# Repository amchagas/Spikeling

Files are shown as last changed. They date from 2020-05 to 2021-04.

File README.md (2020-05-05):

# Welcome to the official Spikeling GitHub

Understanding of how neurons encode and compute information is fundamental to our study of the brain, but opportunities for hands-on experience with neurophysiological techniques on live neurons are scarce in science education. Here, we present Spikeling, an open source £25 in silico implementation of a spiking neuron that mimics a wide range of neuronal behaviours for classroom education and public neuroscience outreach.

For details, please refer to
- the main manuscript on BioRxiv [here](https://www.biorxiv.org/content/early/2018/05/21/327502)
- the entry on Open Labware [here](https://open-labware.net/projects/spikeling/)

Spikeling in action

Spikeling is based on an Arduino microcontroller running the computationally efficient Izhikevich model of a spiking neuron.  The microcontroller is connected to input ports that simulate synaptic excitation or inhibition, dials controlling current injection and noise levels, a photodiode that makes Spikeling light-sensitive and an LED and speaker that allows spikes to be seen and heard. Output ports provide access to variables such as membrane potential for recording in experiments or digital signals that can be used to excite other connected Spikelings. These features allow for the intuitive exploration of the function of neurons and networks.

# Files

In this repository and the associated publication (linked above) you will find all files needed to build a Spikeling, get started with it and do some basic data analysis.

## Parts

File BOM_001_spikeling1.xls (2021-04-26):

BOM: spikeling lite
Item# | Manufacturer | Part # | Qty/PCB | Description | AI/SMD/BGA/PLCC/QFP/ OR Other Part | Designator | Top/Bottom | Comment
1
2 | Arduino | A000087 | 1 | Arduino Nano | Through-hole | MCU | TOP
3 | Samtec inc | SSA-115-S-T | 2 | Headers 15 pin 1 row | Through-hole | J8 | TOP
4 | Alps | RK09K1130AH1 | 4 | 10k/50mw/20% | Through-hole | RV1;RV2;RV3;RV4 | TOP
5 | Murata | PKMCS0909E4000-R1 | 1 | 25V 75dB | SMD | BZ1 | TOP
6 | RS pro | 546-4027 | 5 | female PCB conn | Through-hole | J1;J2;J3;J4;J5 | TOP
7 | TE connectivity | 4-1437565-1 | 1 | 12V 50ma | SMD | SW1 | TOP
8 | BroadCom | HSMF-C155 | 1 | 617nm 2V 20mA | SMD | D2 | TOP
9 | Kemet | C1206C102KDRACTU | 1 | 100V 1nf 5% | SMD | C1 | TOP
10 | Vishay | CRCW120610K0FKEA | 2 | 250V 10k 250mW 1% | SMD | R1,R4 | TOP
11 | TE connectivity | CRG1206F47R | 1 | 250V 47ohm 250mW 1% | SMD | R2 | TOP
12 | TE connectivity | CRG1206F10R | 1 | 250V 10ohm 250mW 1% | SMD | R3 | TOP
13 | Osram | BP 104 S-Z | 1 | visible spectrum photodiode | SMD | D1 | TOP
14 | Cliff | FC68148 DC10A | 1 | Barrel Jack | Through-hole | J6 | TOP
15
16
17
18
19
20
21
22
23
24
25
26
27

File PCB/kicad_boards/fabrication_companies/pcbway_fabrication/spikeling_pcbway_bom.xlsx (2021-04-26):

 |  |  | xxxx xxxx xxxxx xxPCS BOM (Sample Bill of Materials)
Item # | *Designator | *Qty | Manufacturer | *Mfg Part # | Description / Value | *Package/Footprint | Type | Your Instructions / Notes
1 | MCU | 1 | Arduino | A000087 | Arduino Nano | 2.54 through hole | Through-hole
2 | J8 | 2 | Samtec inc | SSA-115-S-T | Headers 15 pin 1 row | 2.54 through hole | Through-hole
3 | RV1;RV2;RV3;RV4 | 4 | Alps | RK09K1130AH1 | 10k/50mw/20% | Through-hole | Through-hole
4 | BZ1 | 1 | Murata | PKMCS0909E4000-R1 | 25V 75dB | SMD | SMD
5 | J1;J2;J3;J4;J5 | 5 | RS pro | 546-4027 | female PCB conn | Through-hole | Through-hole
6 | SW1 | 1 | TE connectivity | 4-1437565-1 | 12V 50ma | 6X6 mm SMD | SMD
7 | D2 | 1 | BroadCom | HSMF-C155 | 617nm 2V 20mA | 1411 smd | SMD
8 | C1 | 1 | Kemet | C1206C102KDRACTU | 100V 1nf 5% | 1206 | SMD
9 | R1,R4 | 2 | Vishay | CRCW120610K0FKEA | 250V 10k 250mW 1% | 1206 | SMD
10 | R2 | 1 | TE connectivity | CRG1206F47R | 250V 47ohm 250mW 1% | 1206 | SMD
11 | R3 | 1 | TE connectivity | CRG1206F10R | 250V 10ohm 250mW 1% | 1206 | SMD
12 | D1 | 1 | Osram | BP 104 S-Z | visible spectrum photodiode | DIL SMT | SMD
13 | J6 | 1 | Cliff | FC68148 DC10A | Barrel Jack | Through-hole | Through-hole
Need a quick and accurante quote? Need an efficient production? Please read SMT Ordering Necessary Files & Info in 1 minute. Thank you very much! (https://www.pcbway.com/smt_ordering_guide.html)
Click for Instructions on How to Create a BOM (https://www.pcbway.com/blog/PCB_Assembly/How_to_Build_a_BOM__Bill_Of_Materials_.html)

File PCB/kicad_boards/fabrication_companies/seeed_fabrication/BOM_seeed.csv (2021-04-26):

Designator | Manufacturer Part Number or Seeed SKU | Qty | Link
J7 | 102010268 | 1 | https://www.seeedstudio.com/Seeeduino-Nano-p-4111.html
J7,J8 | SSA-115-S-T | 2 | https://www.digikey.co.uk/products/en?keywords=SSA-115-S-T
RV1;RV2;RV3;RV4 | RK09K1130AH1 | 4 | https://uk.farnell.com/alps/rk09k1130ah1/pot-rotary-10k-17mm-20/dp/1191725?CMP=GRHB-OCTOPART
BZ1 | PKMCS0909E4000-R1 | 1 | https://www.digikey.co.uk/product-detail/en/murata-electronics/PKMCS0909E4000-R1/490-9647-1-ND/4878401
J1;J2;J3;J4;J5 | 546-4027 | 5 | https://uk.rs-online.com/web/p/coaxial-connectors/5464027/?sra=pstk
SW1 | 4-1437565-1 | 1 | https://www.digikey.co.uk/product-detail/en/FSM4JSMA/450-1129-ND/525821?WT.z_cid=ref_octopart_dkc_buynow&curr=gbp&site=us
D2 | HSMF-C155 | 1 | https://www.digikey.co.uk/product-detail/en/HSMF-C155/516-1456-1-ND/637780?WT.z_cid=ref_octopart_dkc_buynow&curr=gbp&site=us
C1 | C1206C102KDRACTU | 1 | https://www.digikey.co.uk/product-detail/en/C1206C102KDRACTU/399-3437-1-ND/721308?WT.z_cid=ref_octopart_dkc_buynow&curr=gbp&site=us
R1,R4 | CRCW120610K0FKEA | 2 | https://www.digikey.co.uk/product-detail/en/CRCW120610K0FKEA/541-10.0KFCT-ND/1181874?WT.z_cid=ref_octopart_dkc_buynow&curr=gbp&site=us
R2 | CRG1206F47R | 1 | https://www.digikey.co.uk/products/en?keywords=CRG1206F47R
R3 | CRG1206F10R | 1 | https://www.digikey.co.uk/products/en?keywords=CRG1206F10R
D1 | BP 104 S-Z | 1 | https://www.digikey.co.uk/product-detail/en/Q65110A2626/475-1345-1-ND/1227851?WT.z_cid=ref_octopart_dkc_buynow&curr=gbp&site=us
J6 | FC68148 DC10A | 1 | https://uk.farnell.com/cliff-electronic-components/fc68148/socket-pcb-dc-power-2-1mm-pk10/dp/224959?CMP=GRHB-OCTOPART

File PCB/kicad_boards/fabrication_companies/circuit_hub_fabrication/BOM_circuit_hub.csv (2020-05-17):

References | Qty | Description | Manufacturer | MPN | Manufacturer_1 | MPN_2 | Digikey | Mouser | RS | Newark | Farnell
J7;J8 | 2 | Headers 15 pin 1 row | Samtec inc | SSA-115-S-T | Samtec Inc | SSW-115-01-T-S | SAM1122-15-ND |  | 180-4101 |  | 2779587
RV1;RV2;RV3;RV4 | 4 | 10k/50mw/20% | Alps | RK09K1130AH1 |  |  |  |  | 729-3587 |  | 1191725
BZ1 | 1 | 25V 75dB | Murata | PKM22EPPH4001-B0 |  |  |  |  | 516-8252 |  | 1192512
J1;J2;J3;J4;J5 | 5 | female PCB conn | Radiall | R141426161 |  |  | A101972-ND | 501-R141426161 | 721-0291 |  | 4195115
SW1 | 1 | 35V 10mA | E-switch | KS-01Q-01 | C&K | D6C90 F1 LFS |  |  | 102-327 |  | 2522279
D2 | 2 | 617nm 2V 20mA | Knightbright | L-793ID |  |  |  |  | 247-1791 |  | 1142588
C1 | 1 | 100V 1nf 5% | Multicomp | MCRR50102COGJ0100 | Murata | RDE5C1H102J0M1H03A | 490-8962-1-ND | 81-RDE5C1H102J0M1H3A | 1335665P |  | 1216422
R1,R4 | 2 | 250V 10k 250mW 1% | Multicomp | MF25 10K | TE connectivity | CFR16J10K | A104668CT-ND |  | 125-1153 |  | 9341110
R2 | 1 | 250V 47ohm 250mW 1% | Multicomp | MF25 47R | Ohmite | OD470JE | OD470JE-ND | 588-OD470JE | 707-7568 |  | 9341986
R3 | 1 | 250V 10ohm 250mW 1% | Multicomp | MF25 10R | TE connectivity | YR1B10RCC | A105944CT-ND | 279-YR1B10RCC | 1372768 |  | 9341145
D1 | 1 | IR 20° | Osram | SFH203 | Osram | SFH203-FA | 475-1075-ND | 720-SFH203FA | 654-8154 | 94AC4969 | 1212743

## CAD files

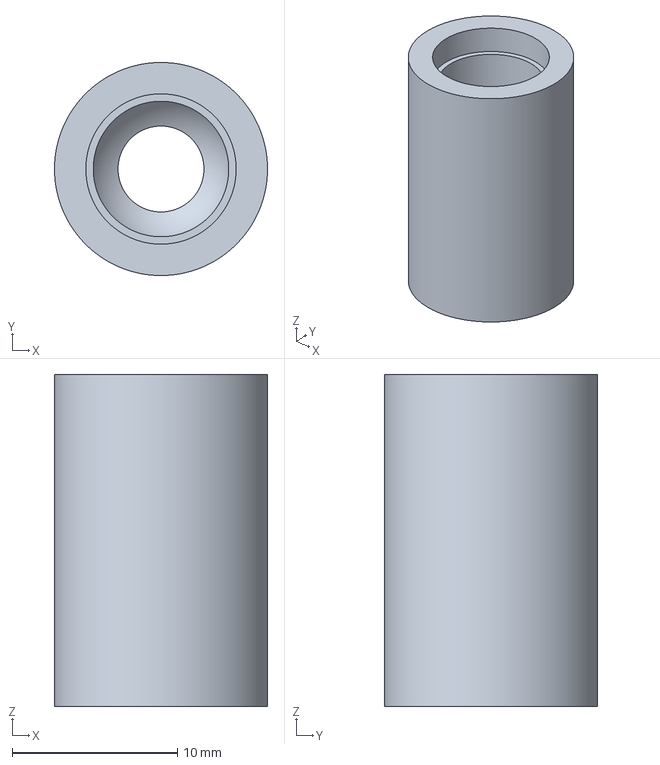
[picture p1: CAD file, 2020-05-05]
3D print/Spikeling LED holder.3mf
12.9 x 12.9 x 20.1 mm

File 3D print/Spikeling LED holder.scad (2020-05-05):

tol = 0.1;
Smoothness = 200;
Wall = 2;

r_LED = 8.9/2;
r_led = 8.0/2;
h_LED = 11.2;
h_LED_base = 2.1;
h_LED_top = 3;

r_photo_base = 6/2;
r_photo = 5/2;
h_photo = 8.9;
h_photo_base = 1;



difference(){
    cylinder (r=r_LED+Wall, h=h_photo, $fn=Smoothness);
    
    #cylinder (r=r_photo_base+tol, h=h_photo_base+tol, $fn=Smoothness);
    translate([0,0,h_photo_base+tol])cylinder(r=r_photo+tol, h=h_photo-h_photo_base+tol, $fn=Smoothness);
}
difference(){
    translate([0,0,h_photo])cylinder(r=r_LED+Wall, h=h_LED, $fn=Smoothness);
    
    translate([0,0,h_photo+h_LED_top])cylinder(r=r_led+tol, h=h_LED-h_LED_top
    , $fn=Smoothness);
    translate([0,0,h_photo+h_LED-h_LED_base])cylinder(r=r_LED+tol, h=h_LED_base, $fn=Smoothness);
    translate([0,0,h_photo+r_led])sphere(r=r_LED+tol, $fn=Smoothness);
    translate([0,0,h_photo])cylinder (r=r_photo+tol, h=h_LED, $fn=Smoothness);
}

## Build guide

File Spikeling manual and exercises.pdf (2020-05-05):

# Spikeling User Manual

## Content

Version 1. 6

th Sept 2018.

## Assembly From Parts

If desired, all parts can be conveniently sourced through Kitspace: https://kitspace.org/boards/github.com/badenlab/spikeling/

When using this option, please be aware:

1) Kitspace will almost certainly not find the cheapest Arduino Nano (clone). You should be able to get one for less than £3. Similarly, PCB manufacturing options suggested may also not be the cheapest. Google is your friend here!
2) Kitspace will likely find some options where “packs” of components are listed (e.g. instead of the 2 optional screws to hold the optional battery pack in place, it may find a box of 100). So, when using the option, do carefully go through the suggested purchase list and edit as appropriate.
3) Obviously, when buying in bulk, things can get a lot cheaper (potentially several-fold savings per unit).

Solder all parts in place as per the below. An introduction to soldering is here: https://www.howtogeek.com/63630/how-to-use-a-soldering-iron-a-beginners-guide//.

For details on parts, see Bill of materials (BOM).

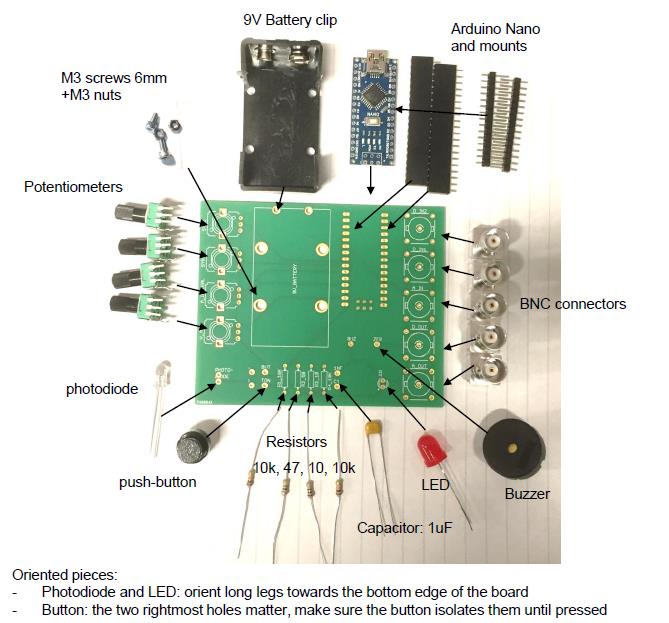
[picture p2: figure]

When complete, it should hopefully look like this:

Note: If it doesn’t seem to work, 9 out of 10 times it’s because 1 of the following:

1) Did you upload the Arduino script? If not sure how to do that, see below under getting started.
2) Somewhere, 2 or more contacts that shouldn’t touch, so in fact touch and thus short-circuit something. Carefully check the board (both sides, solder can leak through the holes and make unwanted contacts on the other side). To check, it can be instructive to “beep” the circuit with a multimeter (google that if unsure). If you have a short circuit, remove it. Usually, simply reheating the pad may do the trick, but if not, used a solder sucker.
3) “Cold contacts”, i.e. an intended contact that are not actually connected. This can easily happen e.g. if the parts are slightly moved during soldering, such that in the last second, as the solder hardens, the pieces come apart. They may then “look” like they are fine, but don’t conduct. Check with multimeter, or simply re-heat all the dodgy looking contacts.
4) Did you solder the oriented pieces the right way round? (see previous page)

You will know if it works if you power it (Battery or USB cable), with all dials turned to midpoint, if you then crank up dial 4 or hold it into the light, it should start to spike (audible clicks coupled to flashes from the LED). Congratulations, you have successfully built a Spikeling!

## Getting Started

Turn all dials to midpoint (you should feel a gentle “click”) and power the board (via USB, or via 9V Battery). The Arduino LEDs should come on. If the board is already on, press the small white reset button on the Arduino itself (not the big black button on the board). This will take a few seconds and puts Spikeling in “reset state” (i.e. mode 1, with all dials to midpoint). All instructions below assume you start from here.

The reset state mimics the “average textbook neuron” - a vertebrate spiking neuron with a resting membrane potential around -70 mV and a spike threshold around -55 mV.

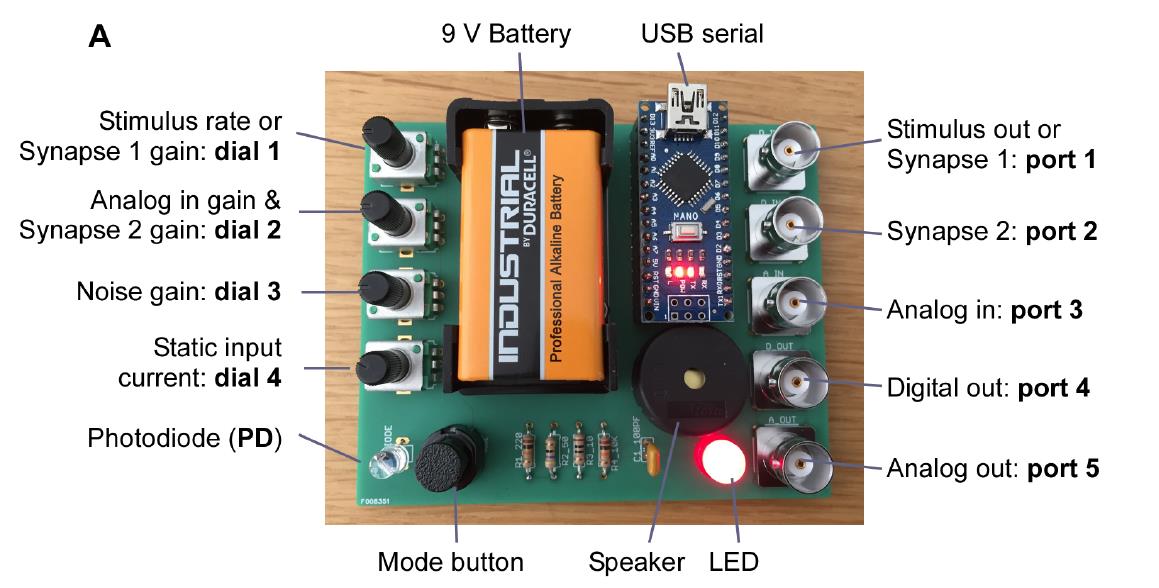
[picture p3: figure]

To visualise and record the activity of Spikeling, there are several options but the best is via a serial connection to a PC through the USB connection on the Arduino. Here we describe how to use the Serial-Oscilloscope software package provided (under creative commons from http://x-io.co.uk/serial-oscilloscope/). This lets you read all output parameters directly from the Spikeling board for display on the screen or for logging. There is also a YouTube video (https://www.youtube.com/watch?v=jgMG0UQ2_pc) demonstrating how to set up the oscilloscope.

1) Make sure the Arduino IDE is installed as you need the driver (www.Arduino.cc). Note that if you are using an Arduino-clone, the standard drivers may not work. In this case, google for the correct ones and install those instead.
2) Declare the serial port. When you plug the USB cable into the PC you may see a message telling you which “COM-port” is being used. This is the “serial port” which you need to set in the menu of the serial oscilloscope. It may just give one option which is then probably the correct one. The COM port is also found under the Device manager.
3) Set the Baud Rate to 230400.
4) The window should now produce a continuous stream of numbers. These are the output values from Spikeling. To plot them, open the oscilloscope(s) under the menu. Spikeling outputs 9 parameters in parallel, but each oscilloscope window can only display 3. If you need parameters further down the list, simply open a second oscilloscope. You can separately adjust the scale of each trace on the oscilloscope by first selecting it (click the “Beam” button) and then scaling it (left-most thin arrows) and off-setting it (big red arrows). You can also trigger the oscilloscope using the menu on the bottom right.
5) To record data, click “log to file”. This will write a text file (comma and tab separated ASCII) with all numbers output from Spikeling. You can look at this output using any common data-analysis software (for example GNU-R, which is free, or Igor Pro or MATLAB, which are licensed).

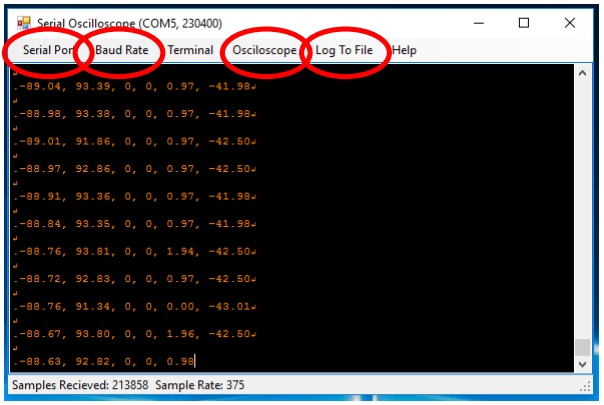
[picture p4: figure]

The output parameters of Spikeling are as follows:

1) Membrane voltage Vm (in “mV“)
2) Total input current Itotal (in arbitrary units). Itotal = IVm + IPD + ISyn1 + ISyn2+ IanalogIn
3) Stimulus state of Synapse 1 port (see below, range 0-1)
4) Synapse 1 state (see below, boolean 0-1 for nospike / spike in the input)
5) Synapse 2 state (see below, boolean 0-1 for nospike / spike in the input)
6) Total photodiode current IPD (in arbitrary units)
7) Total Analog In current IanalogIn (in arbitrary units)
8) Total Synaptic current ISyn (in arbitrary units) ISyn = ISyn1 + ISyn2
9) System time since last reset (in microseconds)

You can also read Spikeling’s Vm output via the BNC ports using a regular oscilloscope. Digital Out only carries the spikes (TTL 5V) while Analog Out on port 5 carries a version of the analog membrane voltage (in arbitrary units). (Note that this output is a pulse-width modulated (PWM) digital signal that is RC-filtered to produce and analog out: it will therefore display filtering artefacts).

Note: If Spikeling is doing “weird things” that clearly does not align with this manual, chances are there is a bad solder contact somewhere – either connecting two pins that should not be connected, or not connecting pins that should be connected (e.g. due to cold solder contacts). Check all contacts carefully and redo them if necessary (i.e. heat them up briefly so they can resettle). It can be worthwhile checking connections with a Multimeter, if available.

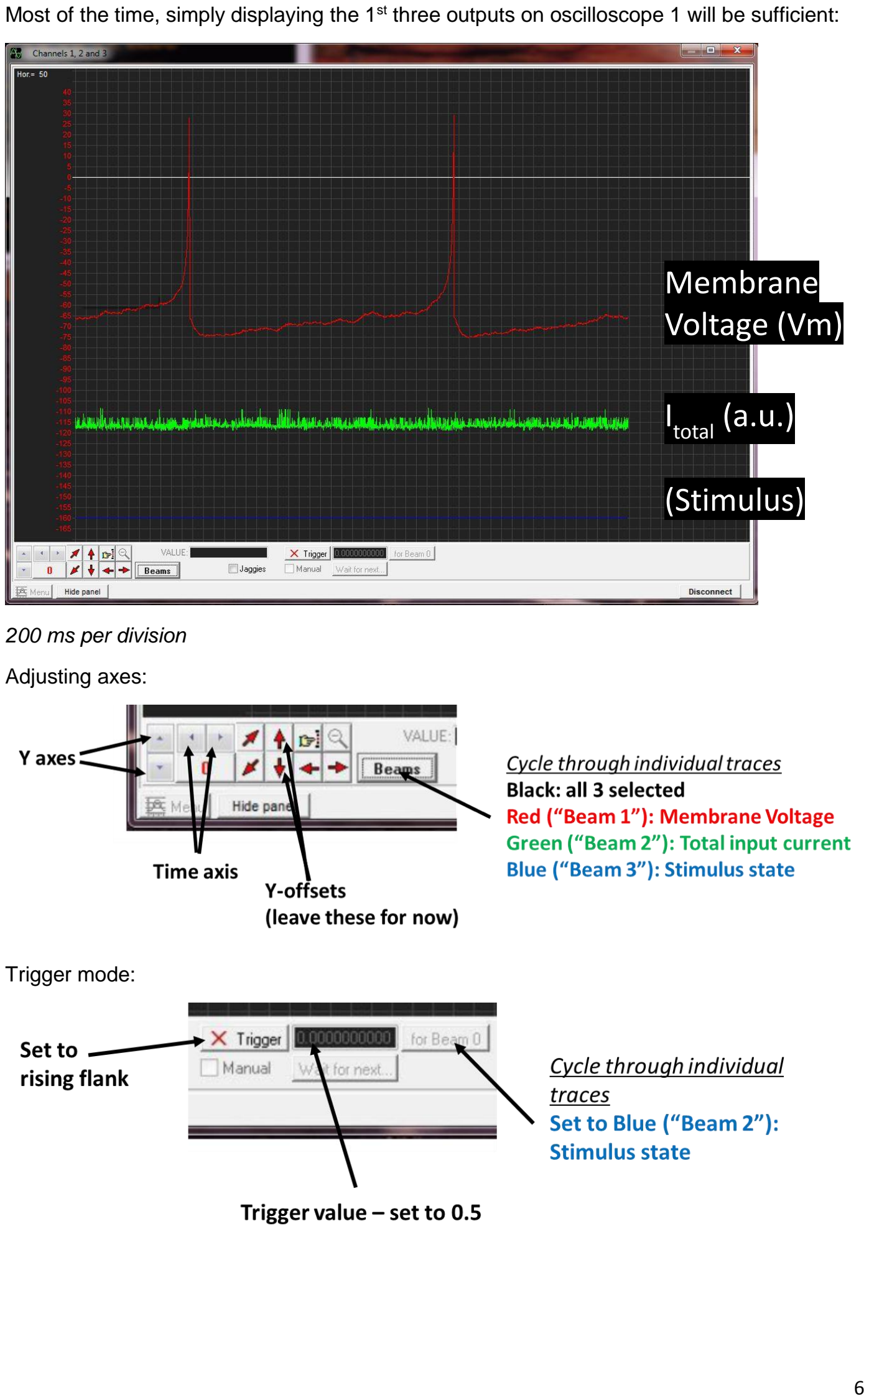
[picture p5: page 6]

Most of the time, simply displaying the 1st three outputs on oscilloscope 1 will be sufficient:

200 ms per division

Adjusting axes:

Trigger mode:

# Membrane Voltage (Vm)

I

# total (a.u.)

# (Stimulus)

## Visualising Spikeling Output with MATLAB

The Serial Oscilloscope plotter saves recordings in comma-separated CSV files. These can be read by a wide range of software: open source possibilities include GNU-R (https://www.r-
project.org), | Python | (https://www.python.org) | or | Octave
(https://www.gnu.org/software/octave/). To comply with software preinstalled on the teaching PCs available at the University of Sussex, we chose to use MATLAB (Mathworks). MATLAB licenses are, however, costly and below we also provide instructions on the use of Python (free!) for visualising Spikeling output.

After opening MATLAB, make sure you have the recorded data and the MATLAB scripts in the same folder. Navigate to that folder (alternatively, the scripts/data may be added to the path.)

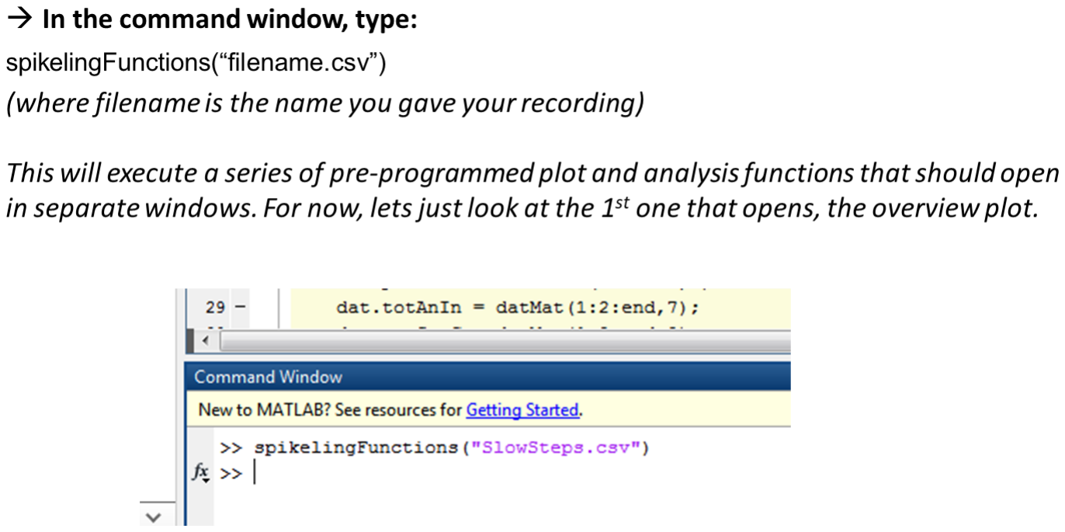
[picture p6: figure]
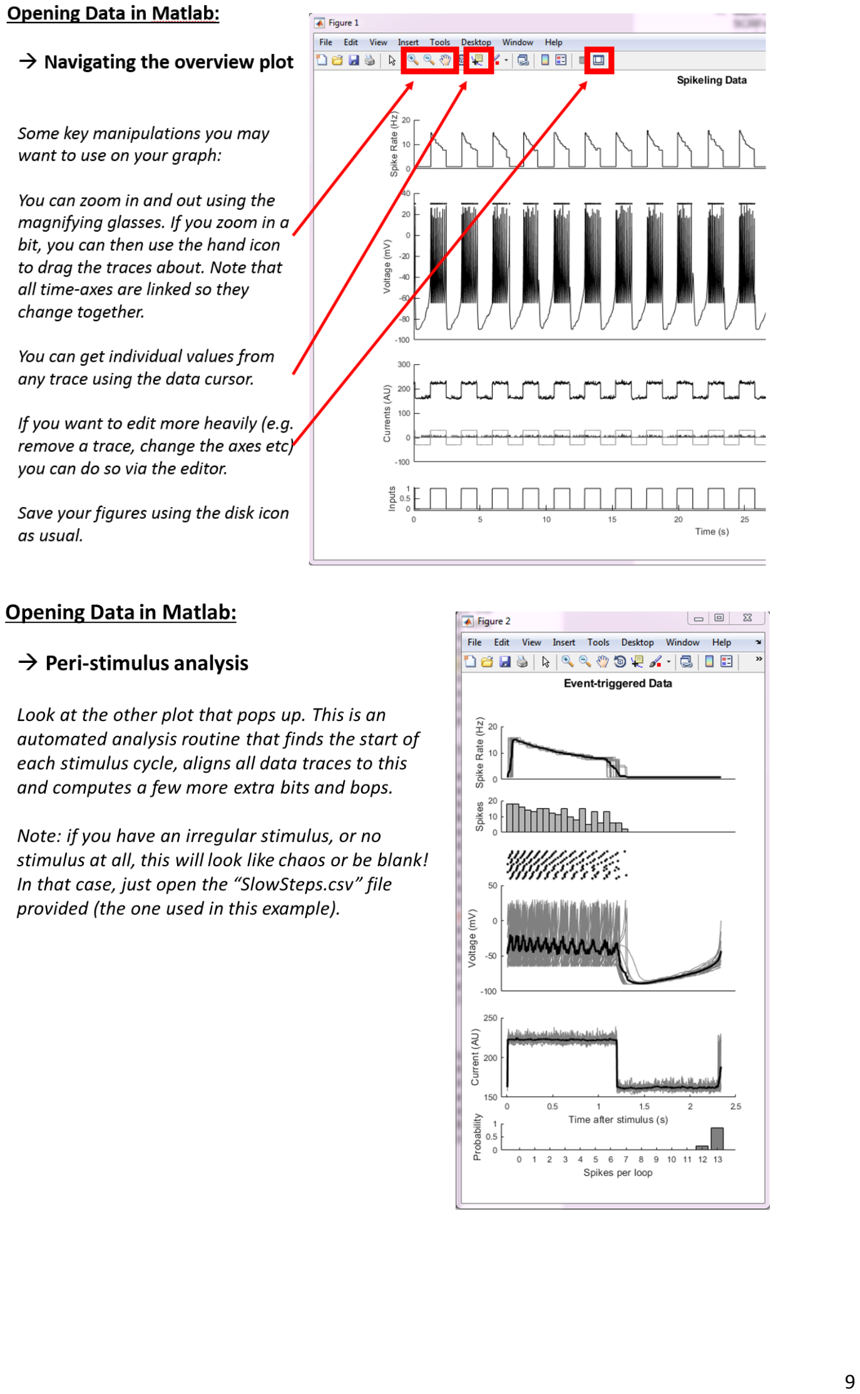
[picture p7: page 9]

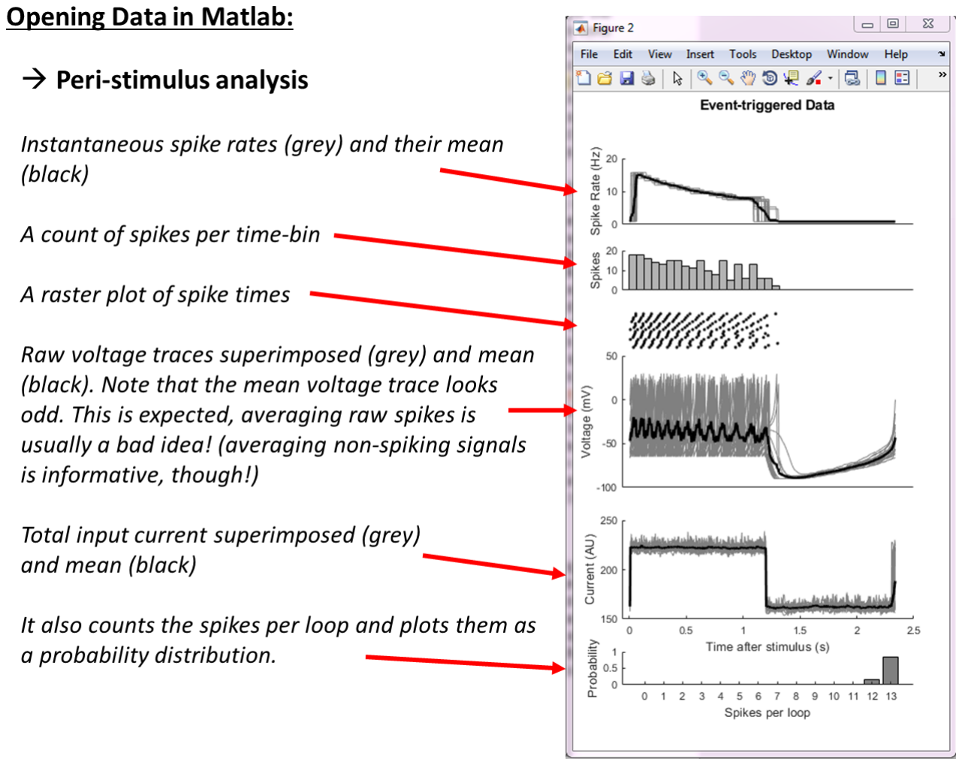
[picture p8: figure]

## Visualising Spikeling Output with Python

We also provide similar scripts in Python (which is free) in the form of a Jupyter Notebook (http://jupyter.org) that reads the serial plotter’s logged csv file, detects spikes, aligns the data in different ways and plots the results in simple graphs. Here we provide a brief explanation of how to run the Python code, rather than a repeat of the detailed explanation of the plot functions.

### Getting started with Python

While the Jupyter Notebook could principally also be executed directly from GitHub without installing Python, this would quickly generate issues with the way that the script provided loads the csv data. For simplicity and convenience, we therefore here give a brief account of how to execute and modify the script in Anaconda.

1) Download Anaconda (it’s free). Navigate to https://conda.io/docs/user-guide/install/, pick the right version for your operating system and follow the install instructions given
2) Once installed, launch a Jupyter Notebook, for example by executing the Anaconda Navigator and clicking “launch” under the corresponding tab. This will open a window in your web browser showing some folders on your home hard drive. Here, navigate to the folder containing the Jupyter script provided (Spikeling Analysis.ipynb) and open that script.

3) Also copy whatever csv file recorded with Spikeling you want to analyse. In the example given below, this will be the file SlowSteps1.csv in the zipped Example Data provided.
4) Your screen should now hopefully look something like this:

### Using the Juypter Notebook

Jupyter notebooks are organised into “cells” (each grey area) which can be called individually. Alternatively, all cells can be called at once (in sequence) to execute the whole thing.

Before doing so, make sure that the file name to be analysed is entered where it says:

data = np.loadtxt(‘SlowSteps1.csv’, delimiter = ‘,’)

i.e. if you wanted to read a file name “SomeNewData27.csv” that line should read:

data = np.loadtxt(‘SomeNewData27.csv’, delimiter = ‘,’)

Now, click on the topmost cell (i.e. where it reads “Load raw data”) and then click “run”. This will execute that one cell and jump to the next (which in this case it doesn’t do anything interesting). If you now keep clicking “run”, it will execute each cell of the script in sequence.

To run the whole thing in sequence (not ideal as the bottom of the script has some optional bits) you can also press the >> button 3 steps to the right of “Run”

Once you reach the first plot, it should open up a new tab that simply plots the raw data (and detected spike times). It should hopefully look something like this:

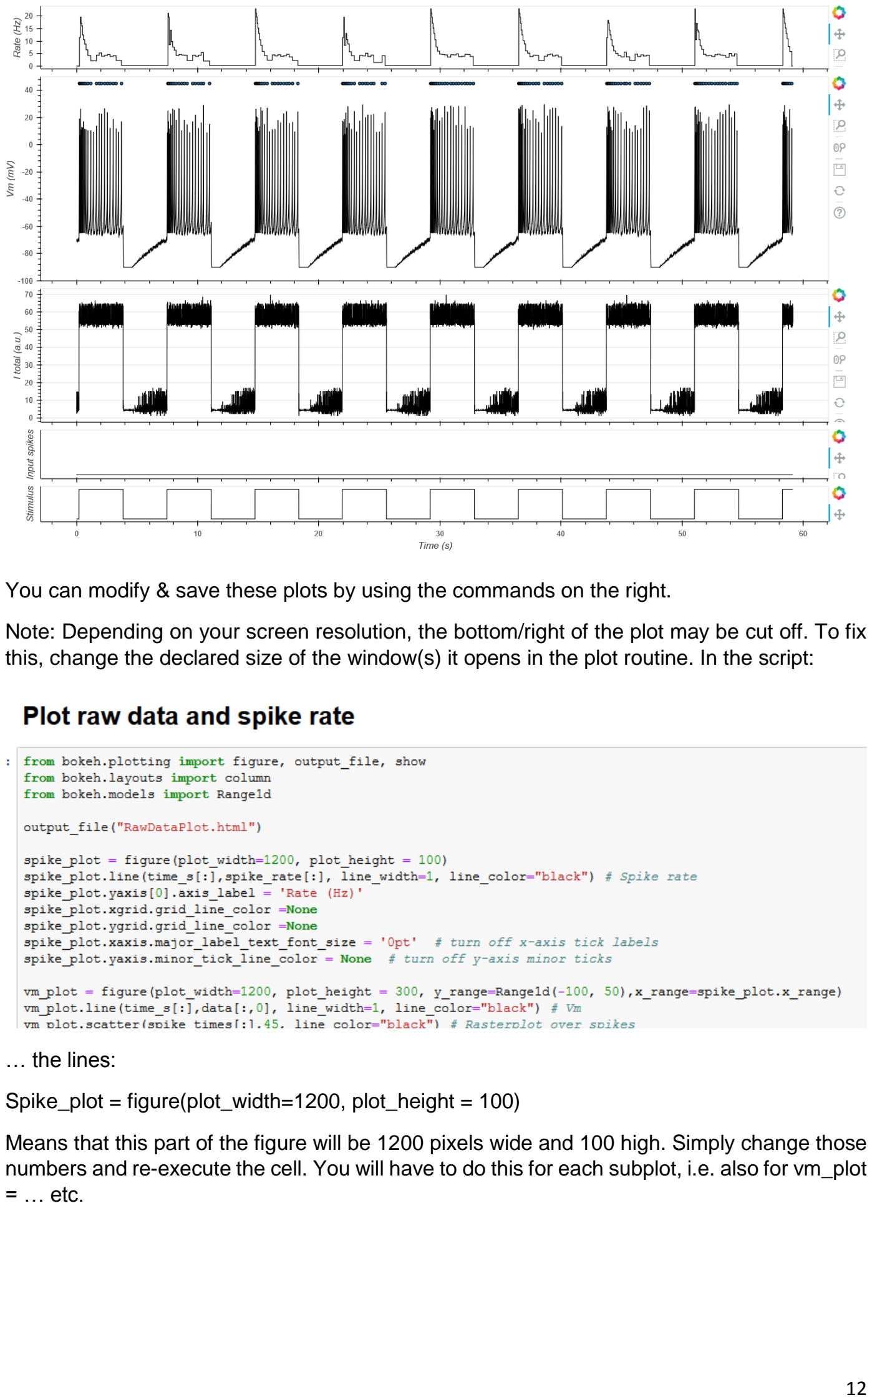
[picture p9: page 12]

You can modify & save these plots by using the commands on the right.

Note: Depending on your screen resolution, the bottom/right of the plot may be cut off. To fix this, change the declared size of the window(s) it opens in the plot routine. In the script:

… the lines:

Spike_plot = figure(plot_width=1200, plot_height = 100)

Means that this part of the figure will be 1200 pixels wide and 100 high. Simply change those numbers and re-execute the cell. You will have to do this for each subplot, i.e. also for vm_plot = … etc.

### Plotting Stimulus aligned data

Following execution of the subsequent the “Analysis Open 1…” cells, a few cells further down, under heading “plot stimulus aligned data” it will generate the stimulus aligned plot. The dimensions of this can be altered in the same way as described above, if required.

### Plotting STAs

Alternatively, if the data is a “noise sequence” generated to recover linear filters (spike triggered averages, STA), skip the whole part that says “Analysis Option 1…” and go straight to “Analysis Option 2: Spike triggered average (STA)”.. Executing this cell will give the STA:

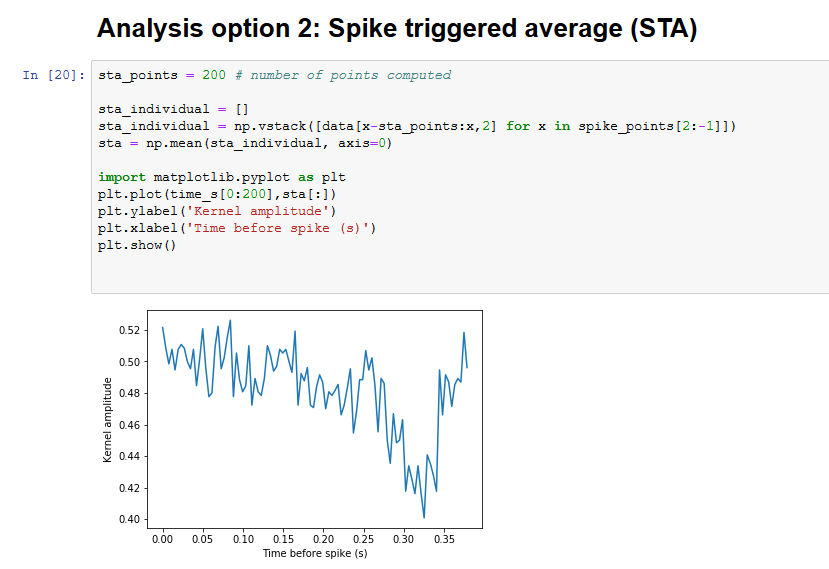
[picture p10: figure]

(here shows the result for the STA of the example data “Noise_Mode3.csv”)

## Reprogramming Spikeling (Arduino)

The “brain” of Spikeling is the Arduino-Nano microcontroller (the blue thing). By tweaking the code that is uploaded here (via the USB cable from the Arduino IDE) it is fairly straightforward to modify Spikeling behaviours, for example by modifying some of the “mode settings”. When opening the Arduino code, in the top there is a list of variables and arrays with some annotations. These should be the 1st point of contact when modifying the code. After each modification, the code needs to be saved and uploaded to the Arduino for the change to take effect.

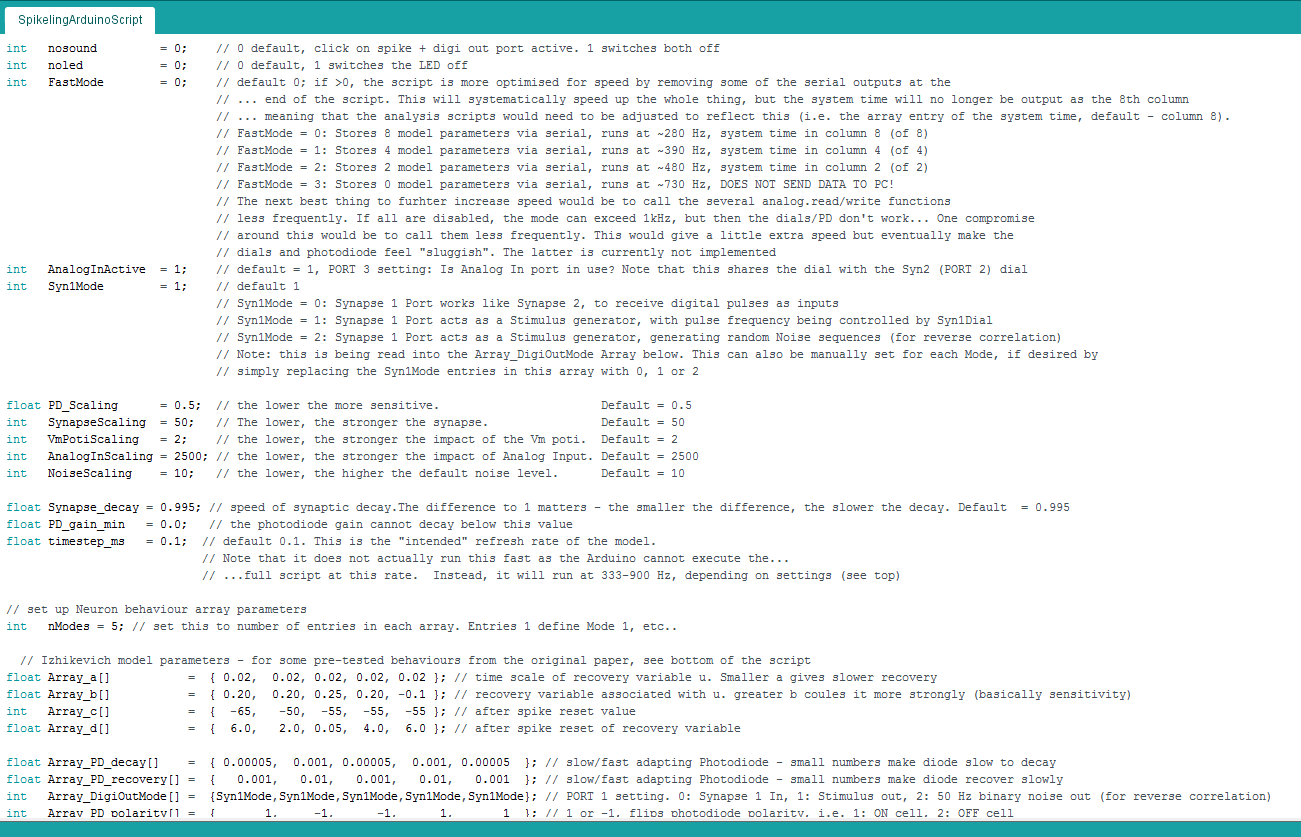
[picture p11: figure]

The screenshot above shows the main variables to tune if desired. For example, replacing the nosound variable currently set to “0” with a “1” will stop the clicking whenever it spikes (note it will also disable the Digi out port as these are on the same connector!).

To modify an existing “mode”, you need to edit the corresponding entries in the 8 arrays listed below “Izhikevich model parameters”. For example, switching the first entry in Array_PD_polarity from currently “1” to “-1” will invert mode 1’s photo-response to make it an “Off-cell”. In the same way, changing the “1” to a “2” will double the gain of the photo-response, etc.

To add new modes, or delete existing ones, simply set the nModes parameter to the new number of entries in each array (must be the same!) and modify the arrays accordingly. For a handy lookup of useful Izhikevich model parameters, scroll to the bottom of the code.

Note: Due to space constraints on the PCB, two Spikeling ports/dials are double booked by two functions. These are:

i) Synapse 1 & Stimulus out use the same port (1), and cannot operate at the same time. This is defined in the Array_DigiOutMode array. “0” enables Synapse 1, “1” enables the 50% duty cycle pulses digi out (default) and “2” enables the 50 Hz noise stimulus used for estimating linear filters (cf. Fig. 6).

ii) Analog In and Synapse 2 gain use the same dial (2). Usually this does not create a conflict as in most cases either Analog In and synapse 2 are not used at the same time. If a conflict arises, it is possible to switch off the Analog In gain using the AnalogInActive variable (set to 0). Advanced users may also choose to re-port these functions in the core code – this would involve resetting the port variables in “void setup” and checking that any use of these ports in the remainder of the code aligns with that change.

### Arduino Implementation of Izhikevich Model

The Izhikevich model is implemented by iteratively computing voltage (v) based on two equations:

(1) v = v + timestep_ms * (0.04 * v * v + 5*v + 140 – u + I_total);
(2) u = u + timestep_ms * (Array_a[NeuronBehaviour] * (Array_b[NeuronBehaviour]*5 – u));

and two conditionals:

(3) if (v>=30.0) {v=Array_c[NeuronBehaviour]; u+=Array_d[NeuronBehaviour];}
(4) if (v>=-90) {v=-90.0);}

In detail:

Lines (1) and (2) are the main model implementations, where…

…we first compute the new value for voltage (v) by adding a quadratic formula of v with recovery variable (u) subtracted, followed by the addition of a single number I_total that reflects the summed input currents (from static input current, photodiode, analog in, synaptic currents etc.)

… and then we re-compute a new value of the recovery variable (u) based on Array entries Array_a and Array_b at position NeuronBehaviour (=the mode, switchable by the onboard button). At default, NeuronBehaviour == 0, so the 1st entries in Array_a and Array_b are used, and when pressing the button NeuronBehaviour is incremented by +1 each time until it resets if it exceeds nModes (further up in the script). The Arrays are found near the top of the script, and reflect the original parameters a, b (& c, d, see below) from the model. Generally, a larger value of u hyperpolarises the model in the next computation of u, as it directly opposes I_total.

In both lines (1) and (2), the increment to v and u is scaled by global variable timestep_ms (default = 0.1). This reflects the “intended” model refresh rate. So, if that set of equations were called 10 times per millisecond (i.e. at 10 kHz) the model would run at “real-time”. However, the actual call-rate is much lower, as the Arduino cannot execute the full script at 10 kHz. In standard configuration, it actually runs at only ~420 Hz. Ways to increase speed are discussed below (“Spikeling Refresh Rate”).

Next, lines (3) and (4) are two conditionals that are triggered as a spike occurs (3) or if membrane voltage drops too low (4).

Line (3) is a carbon copy version of the original Izhikevich model, where upon execution of a spike (v exceeding 30 mV) the model resets the new value of v to be equal to Array_c[NeuronBehaviour] and resets the value of u according to Array_d[NeuronBehaviour].

Line (4) is a custom addition to the model that stops it from hyperpolarising below -90 mV. This is non-essential, but stops the model from crashing if, for instance,I_total becomes too negative to drive unrealistically low membrane voltages.

The functions of Array entries a, b, c and d are explained in detail in the original paper (Izhikevich 2003). The paper and later online additions also give a list of possible “useful combinations” of a, b, c and d that together give the model different “realistic” behaviours. For convenience they are also pasted into the bottom of the Arduino script. To implement them, simply take a specific behaviour’s 1st 4 numbers and add them to the four arrays in the top of the script:

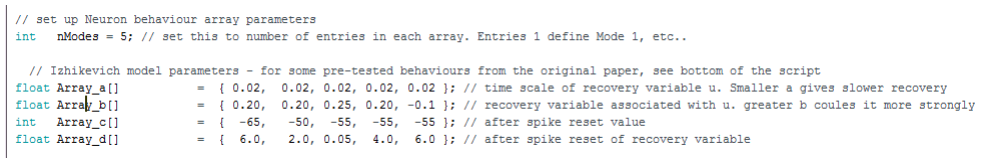
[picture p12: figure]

### Photodiode Adaptation Speed

The photodiode is inherently noisy, so here we use a “buffered time-averaging” of its signal to ameliorate some of the noise. Instead of just reading it’s state on the corresponding AnalogIn Pin (1st line, PDVal) and sending that drive directly into the model as I_PD, we instead send each instance of PDVal into a buffer array PDVal_Array of size 10. Each time the buffer is full (after 10 instances of PDVal being stored in the buffer), we take its mean (PDVal_smoothed) and use that number to inform I_PD.

Next, the Photodiode also has two gain factors (global scaling, and local gain) and two decay constants (time dependent) associated, which allows to have the PD current adapt over time, as it would in most sensory neurons.

- PD_Scaling is global and set at the beginning of the script. This is a single number that scales the amplitude of all PD_related amplitude processes
- PD_gain is the current gain of the PD system. At default, this is 1, but it falls below 1 if the PD in continuously driven, and recovers thereafter as a function of the time-dependent variables, both of which are stored in Arrays at the top of the script and depend on the Mode variable NeuronBehaviour:
- Array_PD_decay[NeuronBehaviour]
- Array_PD_recovery[NeuronBehaviour]
- PD_gain is limited at the top at 1 (full gain), and and the bottom at PD_min (default = 0, which will also have I_PD at 0).
- Finally, as I_PD is being used in the Izhikevich model (see previous section) it is multiplied by either 1 (no change) or -1 (invert), to allow flipping its polarity as a whole thus mimicking “On” and “Off” type behaviour, respectively. This flip is controlled by a third array: Array_PD_Polarity[NeuronBehaviour]

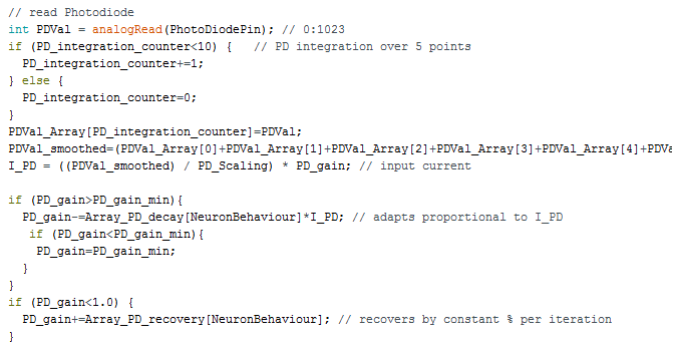
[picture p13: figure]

Photodiode-related arrays at the top of the script:

### Model Noise

Spikeling allows adding synthetic noise to the model, to mimic noisiness in neurons. The noise is added to the I_total variable read in the Izhikevich model as I_Noise. The dial (3) controls the amplitude of the noise around 0 (NoiseAmpl), but has no impact on it’s temporal statistics. This noise function was added in a fairly simple way: At each model instance a single variable I_Noise is increased/decreased by a random amount as a function of NoiseAmpl, followed by a “dampening” step of multiplying the result by 0.9. The dampening step is used to ensure the Noise parameter slowly tends towards 0, as otherwise random noise fluctuations would accumulate to drive sustained de- or hyperpolarising current. Accordingly, the temporal statistics of the noise depend on model refresh rate (see corresponding paragraph below) and this arbitrary dampening factor. We found that a value of 0.9 produces “realistic-looking” noise.

### Spikeling Refresh Rate

The Izhikevich model works by iteratively computing v and u as a function of each other and model parameters a, b, c and d (see corresponding paragraph above). Each time this set of equations is called, the model advances by one unit of time. Accordingly, the more frequently the main loop of Spikeling can execute (“void loop”), the faster the model can run. However, this main loop includes several pieces of code that execute “slowly” (100s of microseconds), limiting the refresh rate. In “standard configuration” (i.e. all parameters set as described in the paper and as provided in the Arduino sketch), the model executes at 420 Hz as 1 full execution round of the void loop takes ~2.4 ms. This leads to a potential conflict: if the Izhikevich timestep parameter (timestep_ms, see above) were set to 2.4 ms to try to achieve maximum speed of the model, it would in fact fail because the model is set-up to mimic fast action potential generation in the mammalian central nervous system where a single spike typically lasts 1 ms at most.

Instead, to get realistic (if slowed down) waveforms of action potentials and subthreshold events, the model should be executed at an intended model rate of ~10 KHz (i.e timestep_ms = 0.1, the default value). Although the model will be executed in 0.1 ms instances, these instances are only called every 2.4 ms so that the model runs ~24 times slower than intended. The waveforms of spikes and subthreshold events continue to look realistic to the observer, they are simply a bit slow. One way to think of this might be to consider Spikeling output as mimicking neurons of cold-blooded animals, where these types of kinetics are commonplace.

### Speeding up the model

If desired, the user can speed up the execution of the model in several ways. Simply put, there are 2 main factors slowing down the loops: Serial Print operations and Analog Read/Write operations. Accordingly, reducing the number of these operations, or the frequency at which they are called will speed up the model.

Serial Print operations are used at the end of the script to log model data via the USB connection to the computer. At default, it logs 9 parameters, in this order:

- Voltage v
- Total current I_Total

- Model Stimulus State Stim_State
- Synapse 1 State (spikes in?) SpikeIn1State
- Synapse 2 State (spikes in?) SpikeIn2State
- Photodiode current I_PD
- Analog input current I_AnalogIn
- Total synaptic current (1+2) I_Synapse
- System time in microseconds currentMicros

Removing some of these from the data logging can increase model speed. If all are removed (no communication with computer), the model refresh rate more than doubles to ~1,000 Hz (loop time ~1 ms).For convenience, we pre-configured a simple option to remove them in several instances through the global variable FastMode near the top of the script. At default (=0), all 9 parameters are logged, and the model runs at ~420 Hz. If set to 1, 2, or 3 the model starts dropping the later parameters, as explained in the script itself (1.57, 1.22, 1.0ms, respectively, corresponding to 633, 819 and 1000 Hz)

(Note: The analysis scripts (Python/Matlab) provided assume that system time, which is always needed for time-accurate plotting, is stored in the 9th column (i.e. 8, with 0 indexing). However, in FastMode=1 or =2, this jumps to column 4 and 2, respectively, so if these modes are used for logging the pre-processing scripts should be updated to reflect this.)

Analog Read/Write operations are called several times within the main loop, either reading the state of a dial, the photodiode or the analog in port (3). Analog write operations drive the Analog out port (5) and the onboard LED. The user could choose to simply disable one or more of these functions. A short explanation how one might go about this is included in the sketch itself. Advanced users may also consider not disabling them, but rather calling them less frequently (e.g. only every 10th time the model loops). While this should principally work, note that it would selectively slow down the instances in which the call was executed, so the model would not run at a constant speed but instead jump a bit. However, this may not be a big problem depending on the intended use. Notably, in the Spikeling 2.0 version (see below) we already down-scaled the Analog read bit depth to 16 to speed them up a little (Using AnalogReadHelper)

Timestep_ms. Finally, the user can also alter the timestep_ms global variable near the top of the script. Increasing this will speed up the Izhikevich model in a linear dependence (i.e. doubling timestep_ms will double model speed) but run risk that it skips spikes and generate weird-looking waveforms. Vice versa, decreasing it will generate “nicer” waveforms, but at further cost to speed. Notably, this will only affect the actual spike model, not the whole script.

## Spikeling 2.0

We are currently working on a new version of Spikeling (2.0) that will feature a range of improvements, including perhaps most notably the possibility to connect a TFT colour display for live display of the model output.

The new version replaces the low-cost Arduino Nano microcontroller of Spikeling 1.0 with the more modern ESP8266 (e.g. https://www.adafruit.com/product/2471). First tests indicate that the ESP8266 (by itself, without TFT screen connected) executes the Izhikevich model at about 5-10 times the speed of Spikeling 1.0 (3.7 kHz at full output, compared to 420 Hz for Spikeling 1). This can be pushed to near “realtime” with fastmode enabled (see above), such that each loop execution round approaches 0.1 ms, which is the iteration step that the Izhikevich model is set to. Of course, it is possible (up to a point) to lower that timestep_ms parameter to match the the actual execution step to achieve “realtime”.

With the screen connected, Spikeling 2.0 speed drops to about the same speed as Spikeling 1.0.

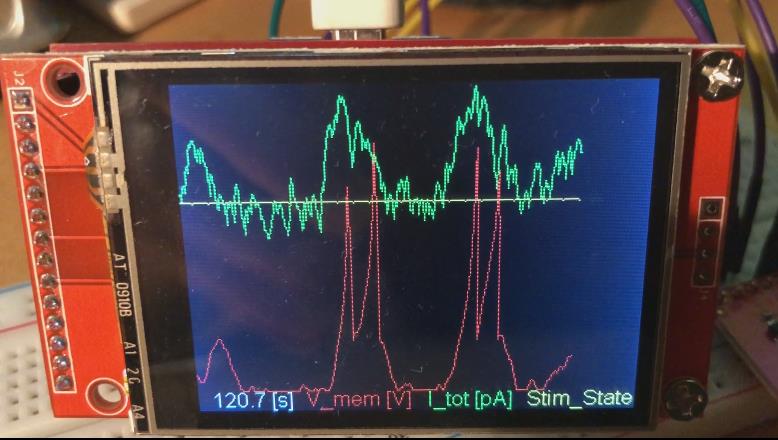
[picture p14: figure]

Spikeling 2.0 prototype with TFT screen connected

In addition to either offering speed enhancements or the option for a TFT screen, the new microcontroller is also WiFi enabled which presents the possibility to do remote-data logging without need for a dedicated USB cable. Notably, to connect the ESP8266 to the dials and photodiode used in Spikeling 1.0 requires addition of a dedicated integrated circuit (IC) chip such as the MCP3008 (e.g. https://www.adafruit.com/product/856).

The ESP8266 Wifi Colour Display Kit sold by ThingPulse, which includes the ESP8266 itself, a breakout board and the TFT screen:

https://thingpulse.com/product/esp8266-wifi-color-display-kit-2-4/ (https://thingpulse.com/product/esp8266-wifi-color-display-kit-2-4/)

At time of writing, Spikeling 2.0 is under

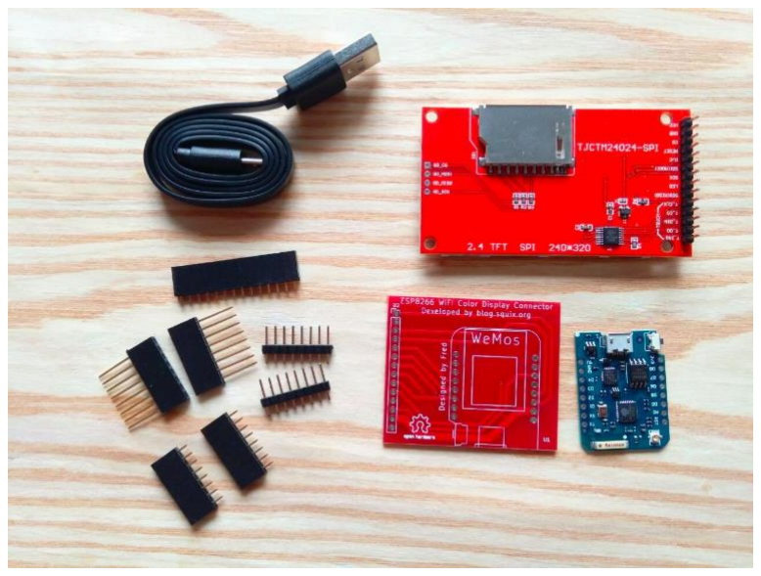
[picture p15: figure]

ongoing development. All documentation to its current state can be found on the Spikeling GitHub: https://github.com/BadenLab/Spikeling. However, the Arduino code running Spikeling

1.0 has already been set-up to work with either version, with one required user alteration depending on which board is used:

//#include "SettingsArduino.h" decommented, so disabled

#include "SettingsESP.h" currently Spikeling 2.0 is enabled.

To switch, just move the // (decomment) to the other line

## Spikeling Exercises

### Resting membrane potential

In the absence of a stimulus, the Spikeling rests at -70 mV and should only spike sporadically. Resting membrane voltage (Vm) can be set indirectly with bottom-most dial (dial 4), which sets a constant input current. For now, on the oscilloscope we are only interested in the membrane potential trace (the red one) and the current trace (the green one). The red LED on the board also tracks Vm, and flashes with each spike which should also be accompanied by a “click”. Electrophysiologists often connect a speaker to their recording of membrane voltage to get a direct audio feedback of what the neuron might respond to.

Task 1: What happens when you increase or decrease the static input current?

You should observe that increasing the static input current drives Vm towards and beyond spike threshold. As you keep driving Vm upwards, you will elicit progressively higher spike rates. This is the simplest of all neuronal codes - the intensity of a stimulus (here, simply the increased input current) is encoded in the frequency of spikes. Imagine you are the postsynaptic neuron and all you see is this spike pattern – you could easily infer from seeing more spikes in close succession that the input to the presynaptic neuron has probably increased. Most spiking neurons use this rate code to signal input intensity.

On the screen, note that each spike is preceded by a shallow rise in Vm and followed by a brief dip below starting levels. This dip is the refractory period of the neuron. During this time, generating another spike is particularly difficult. At the extreme low point of Vm it is impossible to generate a spike, which in a biological neurons is because the sodium channels are blocked (not just closed). This absolute refractory time, together with the duration of the spike itself (1-2 ms) sets a limit on the maximum spike rate possible. In an average neuron, the absolute refractory period is a few milliseconds, and thus the maximal spike rate of most neurons is ~100-200 Hz. Some specialised neurons can go a bit higher, but kHz range is out of question. This means that, by using a single spiking neuron, it is impossible to faithfully encode a time-varying stimulus above this frequency. However, there are a few tricks around this problem that the nervous system can use. We will pick up on this point later.

Task 2: What happens when you dial current up and then wait a few seconds?

If you drive up input current and leave it there for a few seconds, you should observe that spike rate first increases, but then will taper off to some new basal rate of activity which will be higher than the original rate (rate code), but lower than the peak rate. This is an example of adaptation. Neurons respond to a change in the input not only by firing more or fewer spikes, but in addition by adjusting their sensitivity to further changes based on recent stimulus history. This is a fundamental property of neurons that allows them to extend their operating range, and to stay responsive to further changes in subsequent inputs.

Task 3: Does a rapid and a slow current increase generate the same voltage response?

As you increase input current slowly or rapidly, you should observe that you can reach different peak spike rates. A rapid increase in input current is a much more effective way to trigger multiple spikes in close succession. This is again because of adaptation. If you change input current fast enough, the neuron does not have time to adapt and therefore fires vigorously at first. If you change input current slowly enough, you should be able to drive it quite high without eliciting many extra spikes as it adapts while you slowly ramp up the current. This means that not only the absolute level of a stimulus can be encoded by a neuron, by also the rate of change. Note that this creates ambiguity in the code, which is one important reason for the need of parallelisation. This means that if you want to read both absolute levels of a stimulus and its rate of change, you may need two neurons with different properties.

NB: The fact that the speed of change in the input is encoded in a neuron’s firing also means that that spike thresholds are not fixed. Depending how quickly you stimulate a neuron, it can start firing at different Vm values!

### External Stimulation: Light

Spikeling has a built-in photodiode – the clear dome-shaped object in the lower left corner. This functions like a “mini solar-panel”. If you shine light at it, it generates a tiny voltage, and Spikeling is programmed to react to this voltage. Increasing the amount of light hitting the photodiode drives a depolarising current, just like the static input current dial did (above).

Task 4: Shine some light at the photodiode e.g. using a torch or by holding it to the room light. Observe both the current (green) and the voltage trace (red). Can you get the cell to spike in response to light? Does it spike every time you hold it into the light?

Shining light at the photodiode should cause a brief increase in the driving current, which will be mirrored by the membrane voltage. If the light intensity is high enough, you should be able to generate spike(s). However, if the light is weak, or presented only for a very short amount of time, you will probably not drive a spike. This is an example of how neurons can use a spike threshold to only report the presence of a stimulus if it is of a certain amplitude and minimum duration. However, do note that even if there is no spike generated, the membrane voltage will still react to most changes in the light. This “sub-threshold” activity is fundamental to many neuronal computations. We will return to this point later.

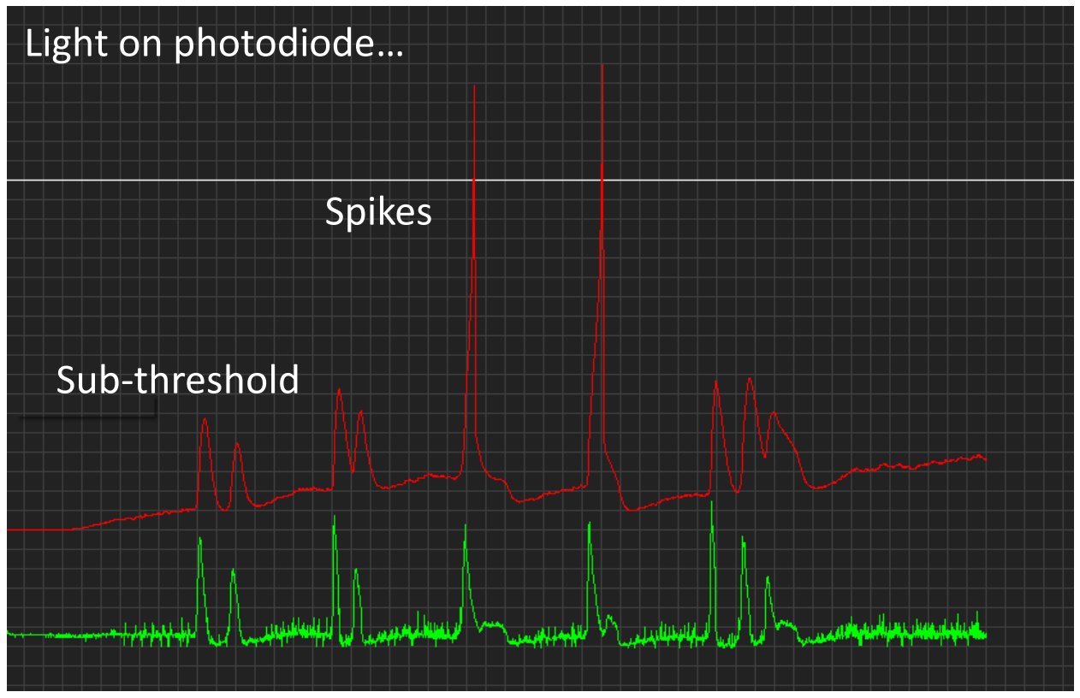
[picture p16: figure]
Spikes; Sub-threshold; Light on photodiode…

Task 5: Turn the static input current dial up so that Spikeling generates a few spikes per second, and then shine some steady light at it. You should observe that the spike rate increases a lot at first, but then settles to an intermediate spike rate (just as before when you increased just the Vm dial). Now, suddenly remove the light. What happens?

You should observe that when you remove the light, membrane voltage will drop not just back to baseline levels, but below baseline for a short period of time. As it drops below baseline, it will probably result in a brief gap in spikes. This is an example of how a sudden absence in a stimulus that the system has adapted to can be encoded by the neuron by the absence of expected spikes. However, the salience of this code is low. For a postsynaptic neuron reading this signal, it is much easier to respond to the presence of an unexpected spike, rather than the absence of an expected one. (How could you turn the absence of an expected signal into the presence of an unexpected one?)

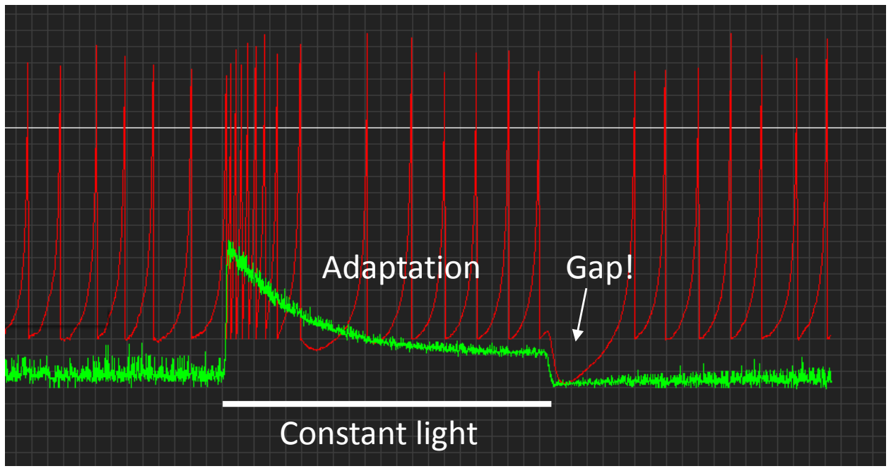
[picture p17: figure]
Constant light; Adaptation; Gap!

## Switching spike-modes

Spikeling comes with multiple preprogrammed behaviours, which can be cycled through with the on-board button (the big black one). If you press the button from reset state, a little LED on the Arduino should light up twice. This means that Spikeling is now in “Mode 2”. If you press it again, it should blink 3 times (Mode 3) and so on. If you get to the end (Mode 5), it will cycle back to 1. You can always jump to 1 by resetting the Arduino (the little white button on the Arduino itself).

The preprogrammed modes are as follows:

1) Regular spiking neuron, slow adapting photodiode (“Sustained ON”)
2) Bursting neuron, fast adapting inverted photodiode (“Transient Bursting OFF”)
3) Fast spiking neuron, slow adapting inverted photodiode (“Sustained OFF”)
4) “Chattering“ neuron, fast adapting photodiode (“Transient ON“)
5) High threshold firing, slow adapting photodiode (“Sustained ON II”)

For now, let’s just focus on the first 3 modes. Compare the above exercises on resting membrane voltage and photodiode stimulation in different spike modes.

Task 6: Comparing Modes 1and 2: What are the differences when you depolarise the neurons using the static input current (dial 4) and when you pass a torch over the diode?

The baseline spiking behaviours, the speed at which the response to photodiode stimulation decays, and the polarity of the light response are all different. For example, if you continuously shine light at Spikeling in mode 1, it will adapt slowly. If you do the same for mode 2, it will adapt a lot faster and to a stronger degree, the current is inverted. This is an example of a “transient OFF” (mode 2) and a “sustained ON” neuron (mode 1). In the nervous system the transience of a neuron is one fundamental ingredient in generating different functions. For example, transient neurons are usually good at encoding the onset of a stimulus, but not very useful in signalling when that stimulus stops. In contrast, the sustained neuron encodes both events quite reliably, but the energetic cost is higher (it needs more spikes) and the information content per spike is lower. Neurons are amongst the most energetically costly cells in the body. They are also amongst the most fragile if energy supply is low (for example during a stroke!). Most neurons will die after even a few seconds to minutes of oxygen deprivation. Accordingly, when considering neurons and neuronal networks, it can often be instructive to consider the energy costs associated with a particular computation. If you can implement the same computation using fewer spikes, or fewer neurons, that is probably a good thing, and most of the time it is what the brain will have evolved to do. Accordingly, it is not always about setting up the “best” computation, often it is about building the cheapest system that still works with adequate reliability.

Another reason for using a transient neuron is that after it signals the start of an event, it is rapidly “ready” to signal the start of another event. If a transient neuron spikes twice, it probably means there were two events. If a sustained neuron spikes twice, it could mean there are 2 events or that there was one event which is still ongoing. Accordingly, the sustained neuron’s code is usually more ambiguous. Ambiguity in coding is almost always a bad thing. It reduces the information content per spike (costly!) and it usually means you need additional neurons to resolve the ambiguity (also costly).

# Light on photodiode – sustained neuron, slow spiking

Task 7: Compare Modes 1 and 3 at the level of the photoresponse and during current injection. What sets them apart?

In Mode 3, the spike threshold is lower and the refractory period following a spike is shorter. This neuron will do most things that the Mode 1 neuron will do, but it will use more spikes. In addition, its photo-response is inverted (“sustained Off cell”). While energetically costly, sometimes you need more spikes. For example, for a rate code to encode as much information as possible, the bigger the rate-range is that the neuron can cover, the more finely resolved can you encode signals using the frequency of spikes. One often used example here are projection neurons of auditory systems.

Another advantage of using a neuron that can reach high spike rates is that negative coding becomes more useful. If the basal firing rate of a neuron is high, a reduction in this rate (for example due to the sudden absence of a depolarising stimulus, or due to the addition of an inhibitory input) can still be readily read out by postsynaptic neurons. This is easily illustrated if you repeat an experiment from above: Set the basal spike rate to a few spikes per seconds using the static input current dial, then iteratively shine a constant light at the photodiode and then remove the light. Each time you shine light, the high “dark” spike rate should drop to a new, lower spike rate, and this change should be much more obvious (and inverted) if you use the fast spiking neuron from Mode 3 compared to the regular spiking Mode 1 neuron.

### The “Self-Stimulator”

From the exercises with the torch, you will have noticed that it is difficult to reproduce the same stimulus from trial to trial. To help you with this, Spikeling comes with an option to “stimulate itself” by generating a defined light output. Port 1, by default, is defined as an output port which delivers 5V pulses at different intervals depending on the mode. Connect a BNC cable to this port, and on the other end connect the extra BNC-cap with an LED attached. You should now see that the LED lights up in regular intervals. Attach this LED to the top of the photodiode (e.g. with a bit of tape or a ring of paper or the 3D printable holder provided) such that whenever the stimulus LED lights up you can clearly see an increase in the input current on the oscilloscope. In addition, configure the 3rd trace on the oscilloscope (blue trace) so that you can see it switch between 0 and 1 to indicate the state of the stimulus.

[Note, instead of using an LED to self-stimulate via the photodiode, you can cut out the middle man and inject by connecting the cable from port 1 to the analog in port (3), thereby driving Spikeling directly with square pulses. For this crank up dial 2 as well to set the gain (amplitude) of this connection].

You should now have 3 traces on the screen: The red membrane potential, the green input current, and the blue stimulus. If you cannot see the stimulus, the y-axis is probably configured incorrectly – use the buttons as described before to adjust the scaling of the blue trace. Every time the stimulus is high, the green trace and therefore the red trace should both respond with an increase in turn. This set-up will let you explore the response properties of Spikeling in a more controlled manner.

For now, let’s focus on Modes 1 and 2. For both, the stimulus LED switches on and off at regular intervals, such that it is on and off exactly half of the time (the technical term is “50% duty cycle”). If you now turn the top-most dial (1) away from resting mid-position, the frequency of this flicker will change accordingly.

Task 8. Stimulate mode 1 at a constant speed (e.g. 1 Hz) and play with the static input current (dial 4). Can you get Spikeling to reliably spike throughout stimulus presentation, but not spike in the absence of a stimulus? How precisely can you encode the end of the stimulus with spikes?

You will probably find that while it is easy to set the neuron to only spike during a stimulus, it is much more difficult to tune it to reliably fire a last spike just before the stimulus ends. This problem will get worse the longer-lasting the stimulus, as the photodiode will adapt just naturally the dropping spike rate. Moreover, any one setting of speed will only “work” with a limited range of settings of static depolarisation. This comes back to the point before – it is much easier to encode the presence of an event with the presence of a spike, than with the absence of an expected spike.

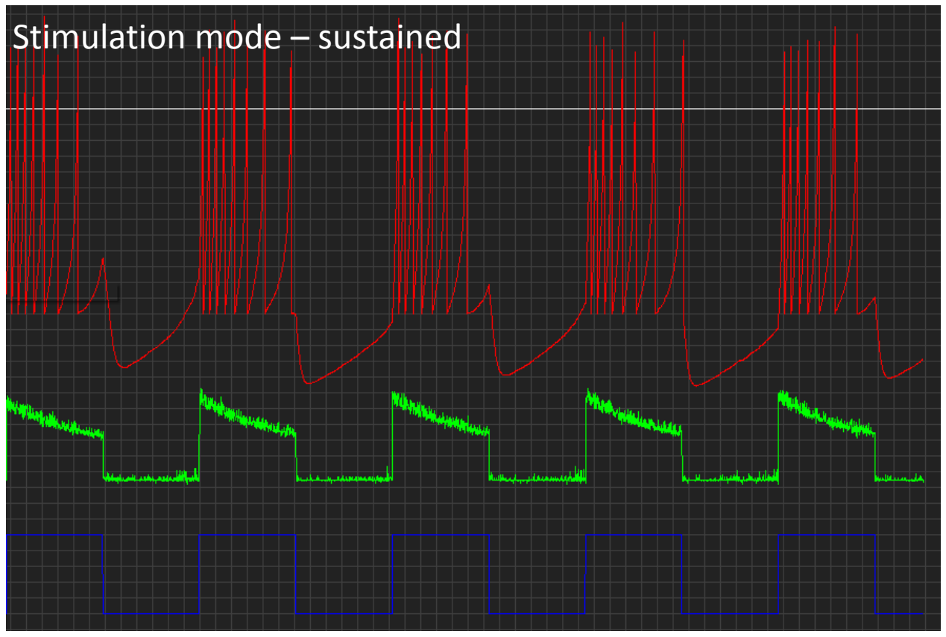
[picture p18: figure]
Stimulation mode – sustained

Task 9. Stimulate mode 2 with steps of light elicited at different speeds. Now, play with the static input current in each mode. Can you get Spikeling to reliably burst during stimulus offset in transient mode 2?

You probably found that it is quite easy to set the transient neuron to encode the offset with a burst of spikes, simply because this is an intrinsically bursting neuron. However, depending on the stimulus speed, you may find that this behaviour breaks down quickly. It is however possible to “entrain” this neuron (synchronise to the stimulus) using light within a limited range of stimulus rates. As such, as a primary sensory neuron reporting the offset of a step of light, this neuron is not great – as it will also spike simply if you wait long enough assuming it is slightly depolarised. However, if you had an inherently rhythmical stimulus (for example a sensory mechanoreceptor neuron in the leg firing during walking) and you wanted to synchronise the activity of other neurons to this stimulus, such a burst-entrainment can be very useful!

Task 11: Now, start playing with the speed of the stimulus while adjusting the static input current as required for all modes. How fast can you go with either the transient or the sustained neurons until you start observing spike failures?

You will probably find that all neurons do a reasonable job in encoding each event with at least one spike until about 2-3 Hz, but that at higher frequencies they will start to fail spiking every now and then despite the presence of a stimulus. As Spikeling is set up, it will probably do a little better using the sustained neurons. This is not inevitable – if one were to change the spiking parameters a bit, it would be possible to make the transient neuron more reliable. More importantly, the photodiode, the spike mode settings and the static input current all come into play when determining thefrequency limit at which a neuron can follow a time-varying stimulus. As such, “tuning” a neuron’s response preference to a desired fluctuating input requires setting a myriad of properties. The nervous system utilises this to tune each neuron to a specific range of input statistics, and, indeed, to adjust these settings as the task at hand requires.

Task 12. Pick one mode and keep increasing the speed of the stimulus almost as fast as it will go and set the static input current such that it only spikes occasionally. What do these spikes encode?

If you set Spikeling into a regime where most stimuli do not trigger a spike, you will notice that nonetheless each stimulus drives a clear subthreshold response. If you now look carefully at the timing of each spike that is elicited, you will likely find that this time is fairly well “phase-locked” to the onset of a stimulus phase. In isolation, this is not a particularly useful property of neurons. But imagine you had 10 such neurons, each spiking unreliably every 5-10 stimulus phases. If you sum the input from these 10 neurons using a larger, postsynaptic neuron, you could fully reconstruct the original stimulus train even though no single input neuron encodes that information. This is called a “volley code”, and it is one of the most important tricks that neuronal networks use to encode a fast time-varying stimulus that exceeds the speed that any one neuron can encode. For example, in auditory systems, the stimulus frequency can easily reach the kHz range which no neuron can possibly follow, as discussed above. Nonetheless, if you record any one neuron’s firing in response to such a stimulus you will probably find that the timing of each spike is exquisitely well phase-locked to the stimulus, such that if you had a few 100 of these neurons you could precisely reconstruct the original input.

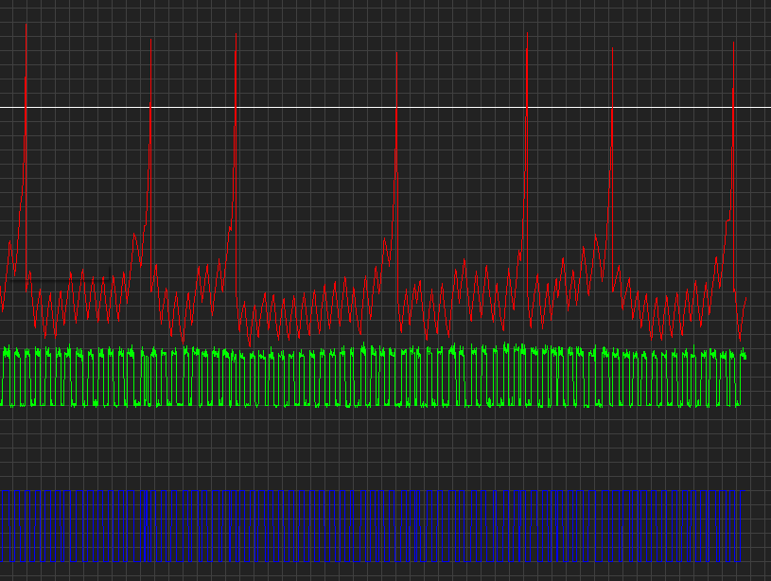
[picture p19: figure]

Task 13. Decrease the static input current until no more spikes are triggered. Observe the membrane potential as you increase the stimulus speed. Can you get Vm to fail following the stimulus?

You will probably find that up to the speed that Spikeling can stimulate, Vm comfortably tracks the stimulus (while spikes do not). This is a fundamental property of neurons. The subthreshold response of a neuron is almost always better at following stimuli than the spike response. As discussed above, eliciting a spike and resetting the neuron to be ready to fire the next spike takes time (in Spikeling, this takes >10 ms, some real neurons can reset after 1-2 ms but not faster). If you do not need to generate a spike, this limitation is dramatically reduced, and you can follow stimuli much better, and much more accurately (also in amplitude). Of course, not all neurons spike. Spiking consumes energy and is a relatively costly and inefficient way of conveying information, so if neurons can avoid using spikes, they will. For example, one fundamental reason to use spikes is to rapidly cover large distances. If you have a big brain (like us), you need to use a spike to send a signal from one end to the other. Depending on a neuron’s electrotonic properties, a graded signal would just decay with

# Stimulation mode

distance and be lost in the noise ~100 microns from the origin. Spikes are regenerative and propagate over distance, allowing signals to be transmitted over longer distances (stubbing your toe). Two disadvantages of signalling with spikes is that you truncate the message, both in time (refractory period) and in amplitude (threshold). So, if the distance to be covered is small, using spikes is usually avoided. For example, the tiny nematode worm C.elegans barely uses any spike at all. The animal is so teeny that all distances are small. Similarly, many neurons in the Drosophila brain don’t spike. Other’s use a “mix” of spiking and graded processing. In vertebrates, the same thing happens in some neurons. For example, in the retina, only about half of the neurons use spikes. Photoreceptors, for example, generally don’t use spikes. Ganglion cells, on the other hand, connect the eye to the brain via the optic nerve – so there is no way around it, those neurons have to spike.

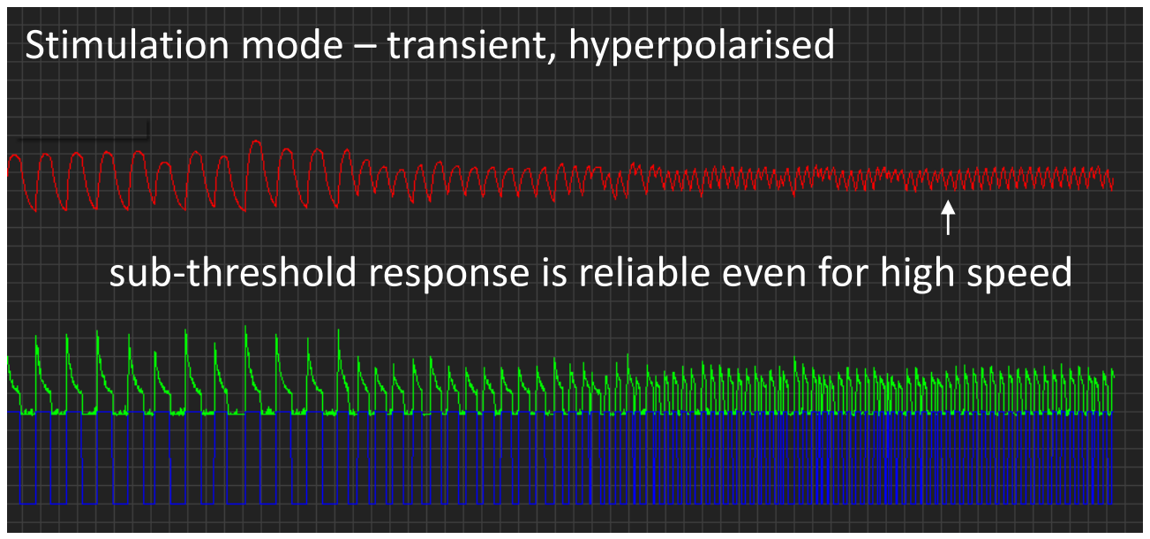
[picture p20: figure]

### Noise

Real neurons are noisy. Sources of noise include synaptic inputs, receptor noise, thermal noise or even noise associated with the physical world that an animal inhabits. Accordingly, one major challenge that all neurons face to at least some degree is how to detect the meaningful “signal” in the background of meaningless “noise”. So far, we have been working at low noise but Spikeling provides the option to add different level noise to any operation – for this, turn the second dial from the bottom (dial 3). At mid-point (reset-state) and below that, no noise is added, but above that position increasing the dial will linearly increase a “noisy current” which adds to the total current shown in the green trace.

Task 14. Turn up the noise dial, while keeping the mean input current roughly centred around 0 (use static input current dial to offset this if necessary). What happens to membrane voltage as you add more and more noise?

At first, increasing the noise current will only affect the baseline noise of membrane voltage, which will resemble a low-pass filtered version of the input noise. This is the first “trick” used by all neurons to dampen high frequency components in the noise – the membrane potential simply cannot track the fastest transients in the input current and therefore “automatically”

# Stimulation mode – transient, hyperpolarised

# sub-threshold response is reliable even for high speed

filters them out. As you keep increasing the noise level, you should be able to elicit spikes. These noise-driven spikes are almost always a bad thing. They do not convey any information (thus wasted energy), and to make things worse, they confound any message that the neuron is aiming to encode using spikes. Accordingly, neurons often aim to keep the spike threshold high enough such that the noise they have to deal with by itself very rarely triggers a spike. Accordingly, spike generation can be used as a powerful noise filter.

Task 15. Turn the noise dial (3) back down and look at the baseline. Now cover the photodiode (e.g. with your hand). What happens?

You will probably find that when you cover the photodiode, the baseline noise that we had all along in the above exercises decreases. Clearly, the photodiode is introducing noise to the system! In this case this is high frequency noise that largely gets smoothed at the level of membrane potential. All sensory processes, whether electronic as here, or in biology, necessarily introduce noise - simply because the apparatus to pick up the desired physical stimulus is never perfect. In vision, for example, the stimulus (photons) is absorbed inside an opsin-type protein by a chromophore. As the photon arrives, it photoisomerises the chromophore and thereby sets a biochemical cascade into action that ultimately results in the opening of ion channels. However, the isomerisation event can also occur “spontaneously” – or rather driven by heat. As such, all sensory systems are noisy, and nervous systems have evolved a wide range of little tricks to overcome this problem. Here, spike generation or the

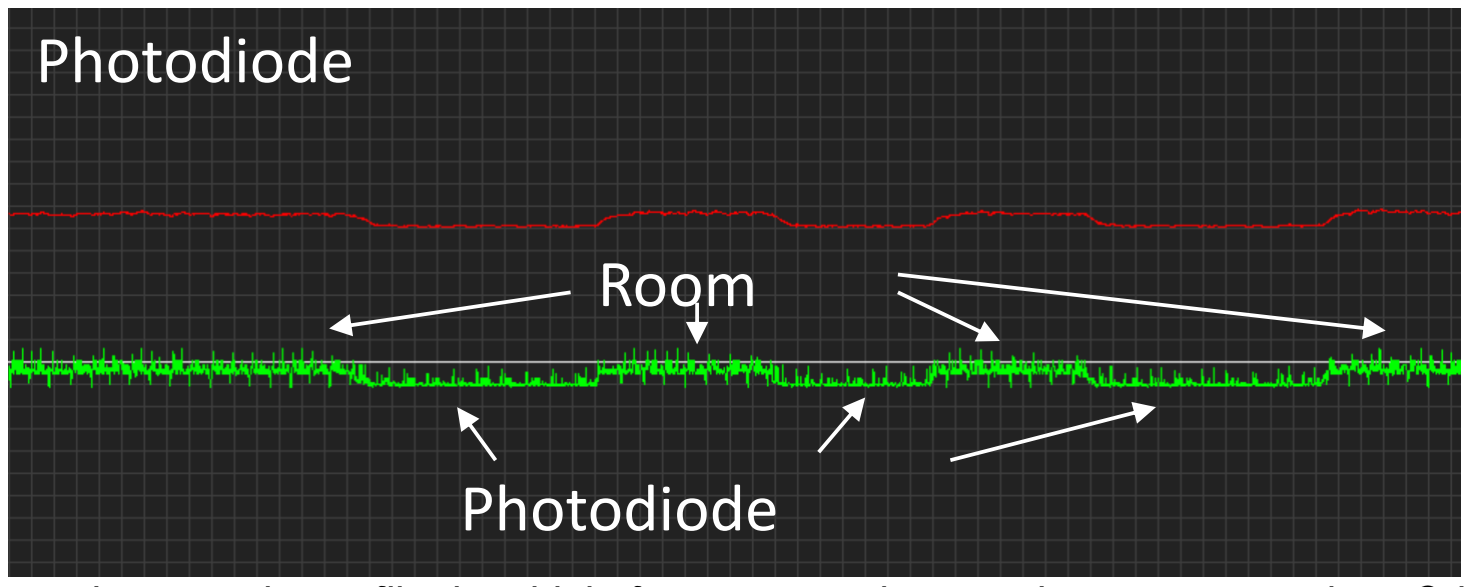
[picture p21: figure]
Photodiode; Room

membrane voltage filtering high frequency noise are but two examples. Others include summation (having multiple neurons signal the same thing and then adding the signal up in a postsynaptic neuron) and temporal “smearing” (e.g. by using slow receptor cascades) are two further examples. There are many more.

Task 16. Compare two modes of your choice to see how each deals with noise. Which one would you use to reliably trigger spikes in response to each stimulus? Which one would you choose to make sure spikes are only elicited at the start of a stimulus (even if sometimes they fail)?

You will probably find that the sustained neurons will be quite good at reliably firing at least one spike in response to each stimulus. However, the number and timing of each spike per stimulus cycle will likely vary a lot. In contrast, the transient ON neuron might fail every now and then to report the presence of the stimulus, but if there is a spike, it usually means that it was preceded by a stimulus. Spikes from such a neuron are highly informative, but unreliable. How can nervous systems make this mechanism more reliable?

### Building networks

Multiple Spikelings can talk to each other using the Digital Out and Synapse 2 BNC ports (or Synapse 1, if enabled in the Arduino code, default is disabled). The idea is that the Digital Out port of one Spikeling (port 4) conveys only spike events, which can be fed into the Synapse 2 input ports of a second Spikeling (port 2). The gain of each synapse can be regulated using the corresponding dial on the other side of the board (dial 2). At reset state, the gain is zero (so the synapse will not do anything if it receives a spike). If you turn the dial up, you get an excitatory synapse. If you turn it below midpoint, you get an inhibitory one.

Try this now: Reset two Spikelings and take a BNC lead to connect the Digital Out port of one (presynaptic) to the Synapse 2 in port of the second. Connect the second Spikeling (postsynaptic) to the PC via the USB cable so that we can read its activity on the oscilloscope. The presynaptic Spikeling does not need to be connected– but it does need to be powered, either using a 9V battery or by plugging the USB into a power socket).

Task 17. In this configuration (above) increase the static input current on the presynaptic neuron so that it continuously fires a few spikes per second. Now observe what happens to the postsynaptic neuron as you turn up the synapse 2 dial to increase its gain.

You should observe that if the dial is at midpoint, nothing much happens – the spikes from the presynaptic Spikeling are still received, but they do not drive any current in the postsynaptic neuron. (Note that you can see the incoming spikes if you open a second oscilloscope – Synapse 2 spikes are on channel 5, so the green channel of the second oscilloscope). Now as you increase the gain you should see that each spike triggers small depolarising current which decays back to baseline within a few 100 ms. If spikes come in a sufficient rate, this input current will start to integrate between successive incoming spikes to further depolarise the cell. If it reaches threshold, spikes should be triggered. The fact that the synaptic current outlasts the duration of the incoming spike is a fundamental ingredient to neuronal processing. It means neurons can “count and calculate” using synapses – sort

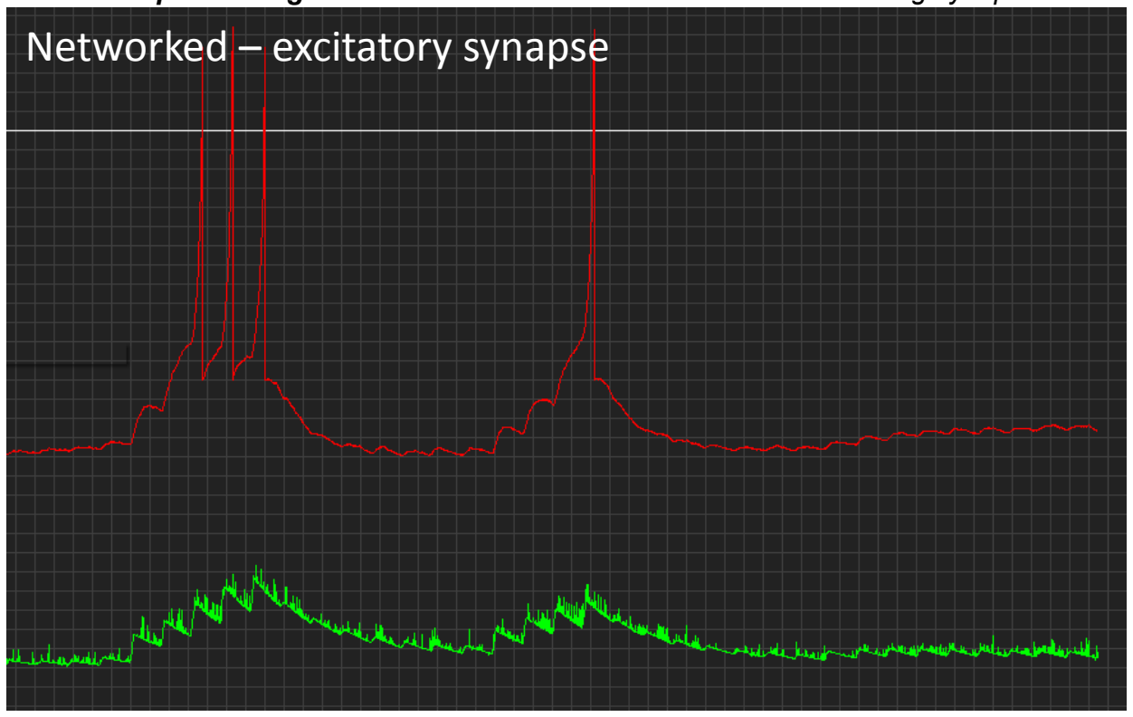
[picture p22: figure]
Networked – excitatory synapse

of, anyway. For example, suppose for a particular computation it is important to know that there was not just one, but two spikes fired within close succession. This could be easily computed by setting the excitatory gain of the connecting synapse(s) such that a single spike does not drive the postsynaptic neuron to threshold, but that if two spikes arrive in close succession, threshold is reached and thus the neuron fires. The same logic also applies across different synapses, which allows the implementation of coincidence detection.

Task 18. Now turn the Synapse 2 dial below midpoint. What happens?

You should observe that now each presynaptic spike drives a hyperpolarising current in the postsynaptic neuron. This is intended to mimic an inhibitory connection. In case of Spikeling, this connection is programmed to be mirror symmetric to the excitatory connection in every way. However, in reality the gain and time courses of synaptic events can vary dramatically and are another fundamental ingredient to building computational networks. For the purpose of this tutorial, the time-course of the synapses is fixed. However, advanced users can change this in the annotated Arduino code.

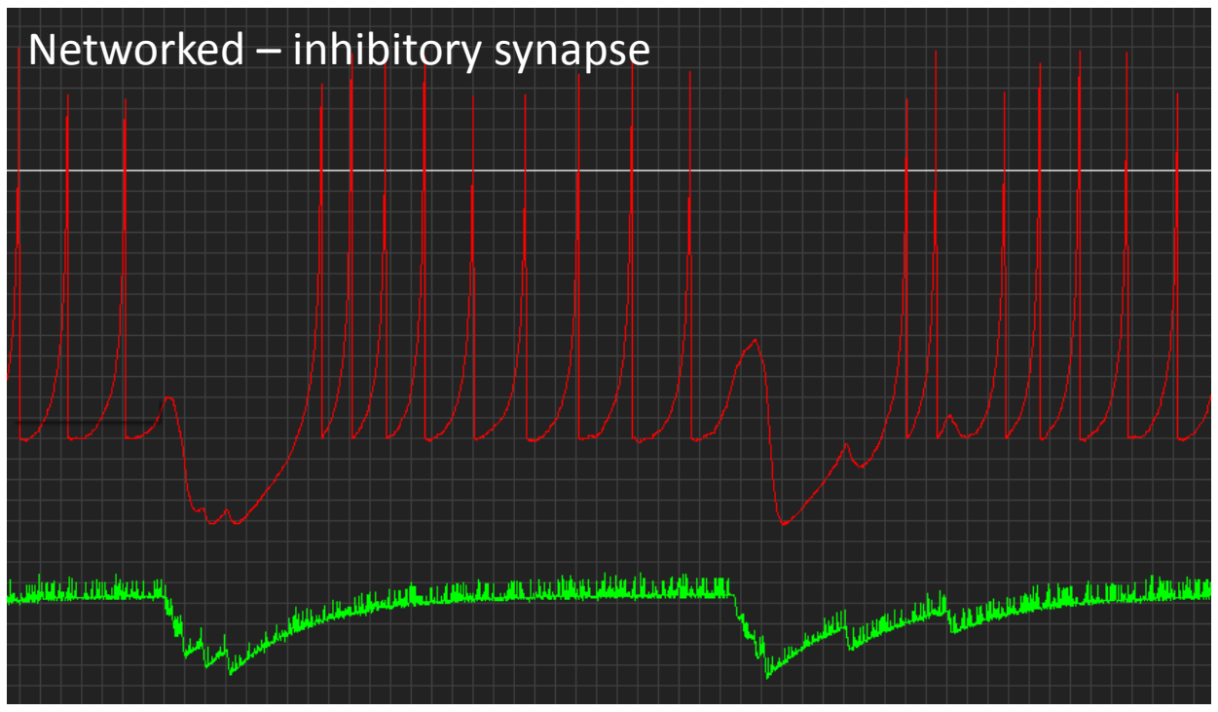
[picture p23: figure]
Networked – inhibitory synapse

Task 19. Put the postsynaptic neuron’s stimulus LED above the photodiode as before, but now hyperpolarise it using the static input dial such that the LED alone does not elicit spikes. On the presynaptic neuron, make sure that it does not fire spikes at rest, and configure its input to be weakly excitatory. Now take a torch to stimulate the photodiode on the presynaptic neuron and thereby make it spike. Can you get the postsynaptic neuron to spike?

Neither the stimulus light nor the synaptic excitation alone should be sufficient to drive a spike in the postsynaptic neuron. However, if you make the presynaptic neuron spike using the torch at the same time as the stimulus comes on, the two excitatory inputs will summate and you should be able to reach threshold. This is an example of a coincidence detector. If the postsynaptic neuron spikes, it means that both the stimulus (stimulator) AND the presynaptic stimulus (torch) were both active at the same time.

One “famous” coincidence detector is used in auditory systems for comparing the signal between two ears. Imagine sound coming from your left. Because sound travels slowly (330 m/s) it will arrive at your left earhole about a millisecond before it arrives at your right earhole. Neurons in each ear’s cochlea will spike as soon as the sound arrives and send that signal to the brainstem where the signals from the two ears are combined. Here there are bilateral neurons that receive inputs from both ears. These are the coincidence detectors. If the sound came from the left, the spike from the left ear comes in before the spike from the right ear and its associated postsynaptic current will decay rapidly, such that it does not overlap with the current triggered by a spike from the right ear. As a result, the central neuron will not spike. However, if the sound comes from e.g. straight ahead, it will reach both ears are the same time which in turn means that the left and right spike inputs to the central neuron will coincide and drive a postsynaptic spike. Such as central neuron therefore encodes the direction of sound. If we now slightly offset the speed by which the spikes travel, or implement delays of initial spike generation in either ear, we can build a neuron that is selective for any sound direction in the azimuth plane (horizontally around the head).

This kind of logic expands into a multitude of computational operations. The above coincidence detector is perhaps the simplest of logical operations: an “AND” gate. This means that Input 1 AND Input 2 need to be “high” for the spike to be triggered. Another logical operation is an “OR” gate – Input 1 OR Input 2 need to be high. This is easily achieved by increasing the synaptic gain such that one neuron alone can drive the postsynaptic spike. There are many such logical operations (e.g. NOR, XOR, XNOR), which can be thought of a computational building blocks of electronics and neuronal networks alike. If you simulate many neurons in a computer, it is straightforward to implement any of these logical gates. We can try to set-up some of these using Spikeling. For example, how might you build an “inverse conditional” – i.e. a neuron that only fires if input 1 is high, unless input 2 is also high? How might you build a NOR gate (only fires when both Inputs 1 and 2 are “low”). How might you build an NAND gate (fires always except when both 1 and 2 are “high”). If you have more than two Spikelings at hand, try playing with these a bit. What kind of computations can you implement? (one useful reference for logical gates and their implementation and background can be found on Wikipedia: https://en.wikipedia.org/wiki/Logical_connective).

Note that in their “pure form”, logical operations are Boolean (“True or False, no intermediate state is possible”). But neurons are noisy, so not all operations are equally “easy” to implement! (all are possible though).

Task 20. Using what you have learnt(!) (and two Spikelings): Can you build an “OFF neuron” using only ON neurons as the input?

One way of doing this is by setting the postsynaptic neuron at a high resting potential such that it continuously generates spikes. Now take a presynaptic neuron that responds to the light in an “On fashion” and connect it to inhibit the continuously active cell. If you tune the inputs right, you should be able to generate something like the below:

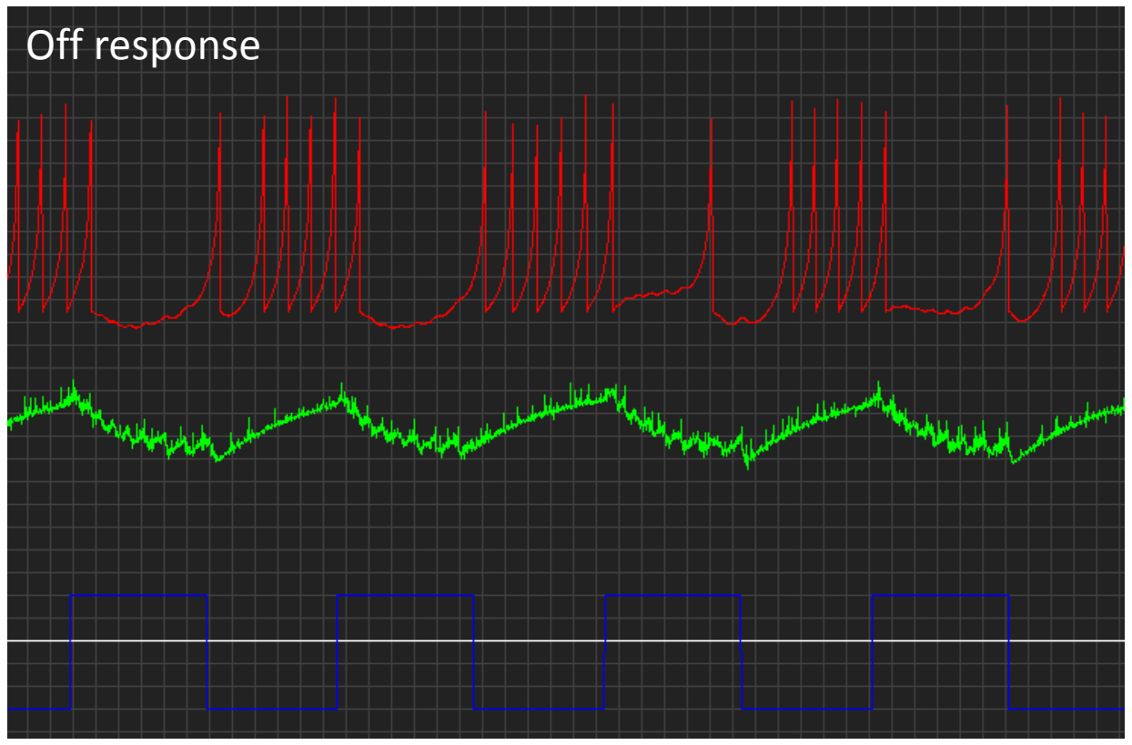
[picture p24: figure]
Off response

This is not a very “good” Off cell. It is a bad Off cell. Sometimes it spikes during the light, and more problematically, the timing of the 1st spike after the light switches off is very variable. This is because now we are not using the presence of an excitatory drive, but rather the absence of an inhibitory drive as signal to generate spikes. Using this setup, you will find it very difficult indeed to tune the off cell to become more transient. The problem is that the synaptic current of the inhibition is slow to decay so after the stimulus switches off the inhibition will take a while to settle back down to zero. This results in a slow upwards trend of the membrane voltage which, as we saw in the beginning, is a very ineffective way to trigger spikes. So, to make it a “better” Off cell, we would need to implement something that makes the membrane potential increase more rapidly after the inhibition turns off. One way to achieve this would be the implementation of a “rebound spike, while another would be the use of a graded (non-spiking) network feeding into Spikeling (as we saw before, membrane voltage is much better at tracking fast inputs below spike-threshold). While Spikeling could principally be programmed to mimic either or both of these possibilities, we will not be covering them here.

Task 21. Using what you have learnt (and two Spikelings), can you build a “delayed ON neuron”? This is a neuron that responds with spike(s) after the onset of a stimulus, but with a delay?

One way of implementing this delayed ON cell would be to use an excitatory synapse that requires more than one presynaptic spike to trigger a postsynaptic spike as shown below. Note the two separate small depolarising current that precede each other by ~100 ms – these come from the presynaptic neuron responding to the light with 2 spikes in close succession. The second incoming spike takes the postsynaptic neuron past threshold.

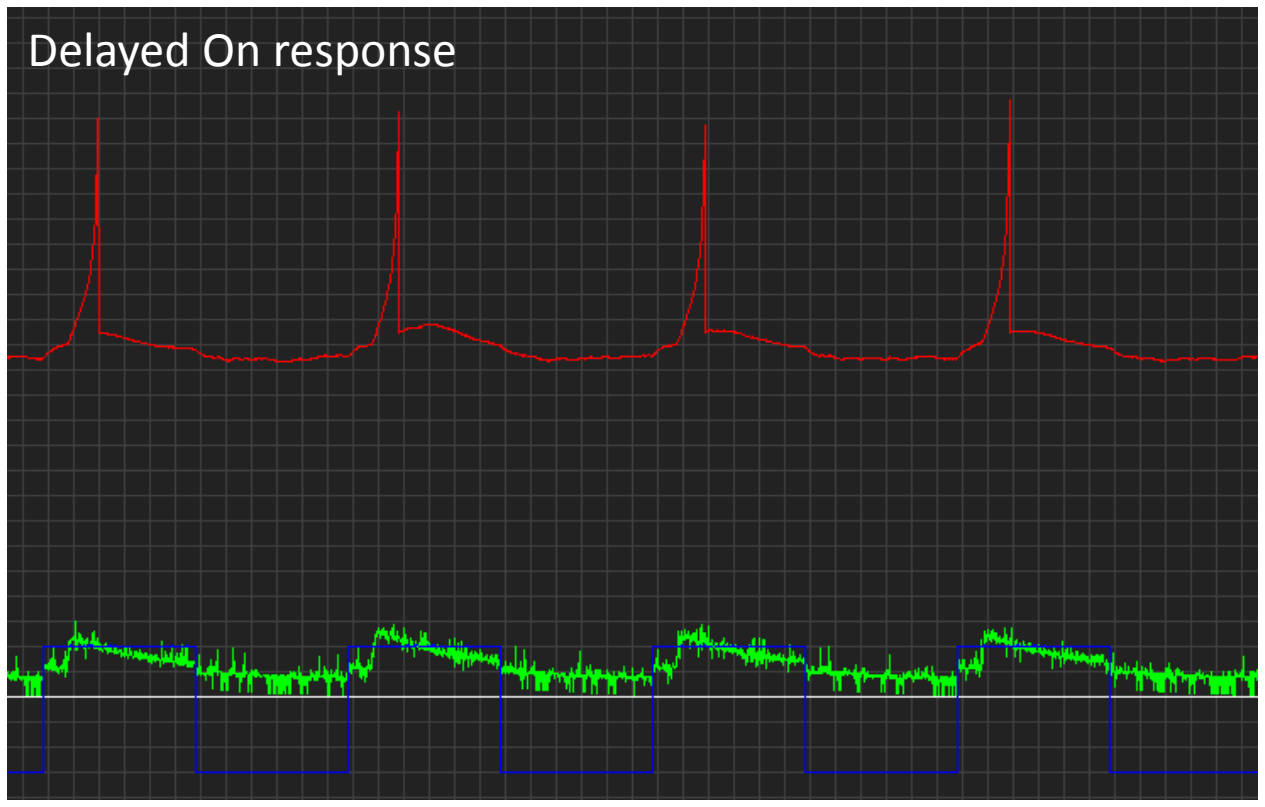
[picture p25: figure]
Delayed On response

Task 22 (final!):

Using the delayed ON neuron circuit, plus an additional non-delayed ON transient neuron, can you build an elementary motion detector? (Hint: This will probably require

### 3 neurons!)

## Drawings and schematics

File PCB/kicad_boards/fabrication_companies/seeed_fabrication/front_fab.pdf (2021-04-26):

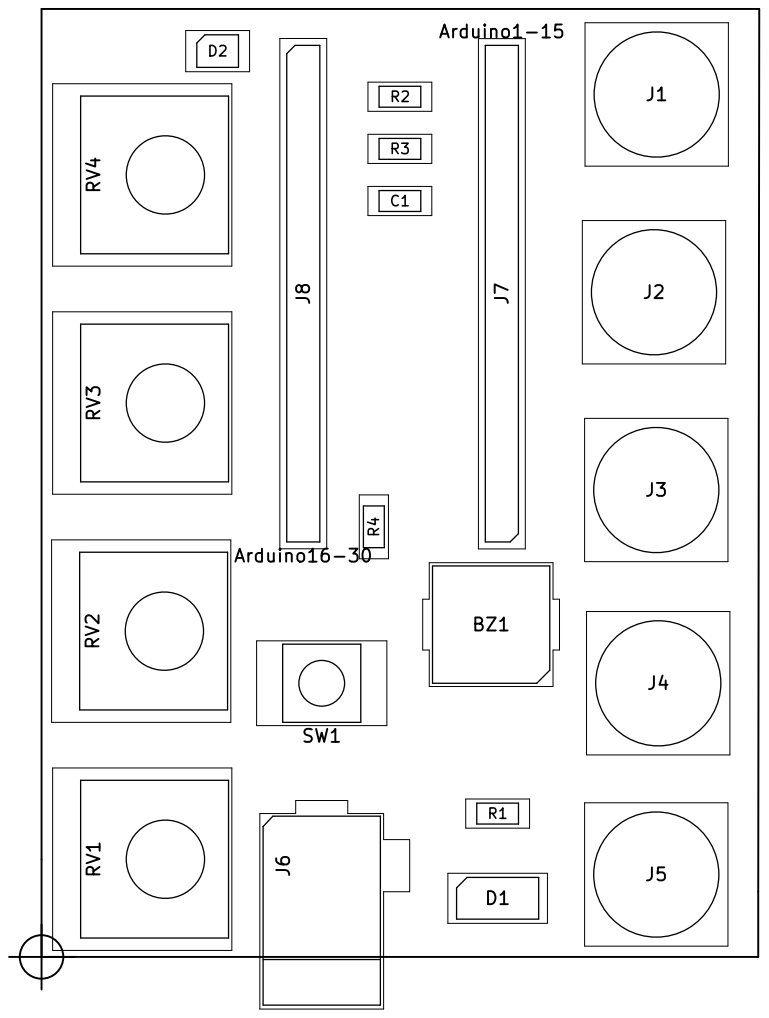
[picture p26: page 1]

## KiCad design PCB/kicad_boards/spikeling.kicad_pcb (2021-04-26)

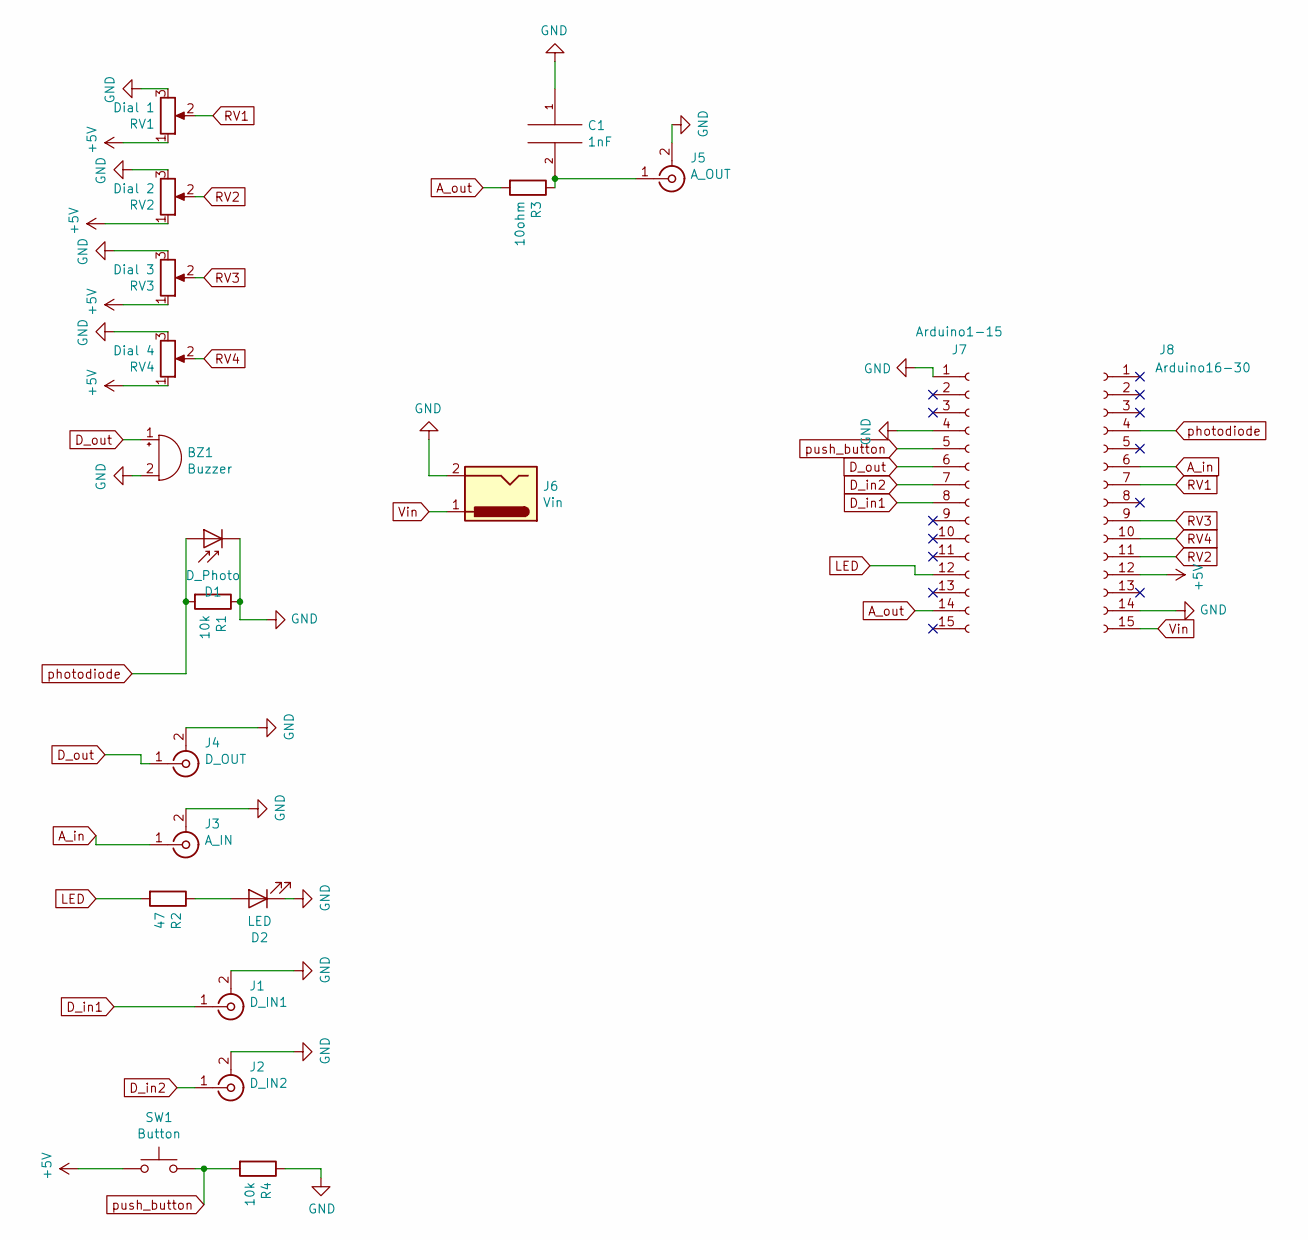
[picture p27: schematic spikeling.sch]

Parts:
BZ1: Buzzer; Buzzer_Murata_PKMCS0909E4000-R1
C1: 1nF; C_1206_3216Metric_Pad1.42x1.75mm_HandSolder
D1: D_Photo; LED_2512_6332Metric
D2: LED; LED_1210_3225Metric_Pad1.42x2.65mm_HandSolder
J1: D_IN1; BNC_TEConnectivity_1478204_Vertical
J2: D_IN2; BNC_TEConnectivity_1478204_Vertical
J3: A_IN; BNC_TEConnectivity_1478204_Vertical
J4: D_OUT; BNC_TEConnectivity_1478204_Vertical
J5: A_OUT; BNC_TEConnectivity_1478204_Vertical
J6: Vin; BarrelJack_Horizontal
J7: Arduino1-15; PinHeader_1x15_P2.54mm_Vertical
J8: Arduino16-30; PinHeader_1x15_P2.54mm_Vertical
R1, R4: 10k; R_1206_3216Metric_Pad1.42x1.75mm_HandSolder
R2: 47; R_1206_3216Metric_Pad1.42x1.75mm_HandSolder
R3: 10ohm; R_1206_3216Metric_Pad1.42x1.75mm_HandSolder
RV1: Dial 1; Potentiometer_Alps_RK09L_Single_Vertical
RV2: Dial 2; Potentiometer_Alps_RK09L_Single_Vertical
RV3: Dial 3; Potentiometer_Alps_RK09L_Single_Vertical
RV4: Dial 4; Potentiometer_Alps_RK09L_Single_Vertical
SW1: Button; SW_Push_1P1T_NO_6x6mm_H9.5mm

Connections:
+5V: J8.12, RV1.1, RV2.1, RV3.1, RV4.1, SW1.1
A_in: J3.1 (In), J8.6
A_out: J7.14, R3.2
D_in1: J1.1 (In), J7.8
D_in2: J2.1 (In), J7.7
D_out: BZ1.1 (-), J4.1 (In), J7.6
GND: BZ1.2 (+), C1.1, D1.1 (K), D2.1 (K), J1.2 (Ext), J2.2 (Ext), J3.2 (Ext), J4.2 (Ext), J5.2 (Ext), J6.2, J7.1, J7.4, J8.14, R1.1, R4.1, RV1.3, RV2.3, RV3.3, RV4.3
LED: J7.12, R2.2
unnamed: C1.2, J5.1 (In), R3.1
unnamed: D2.2 (A), R2.1
RV1: J8.7, RV1.2
RV2: J8.11, RV2.2
RV3: J8.9, RV3.2
RV4: J8.10, RV4.2
Vin: J6.1, J8.15
photodiode: D1.2 (A), J8.4, R1.2
push_button: J7.5, R4.2, SW1.2

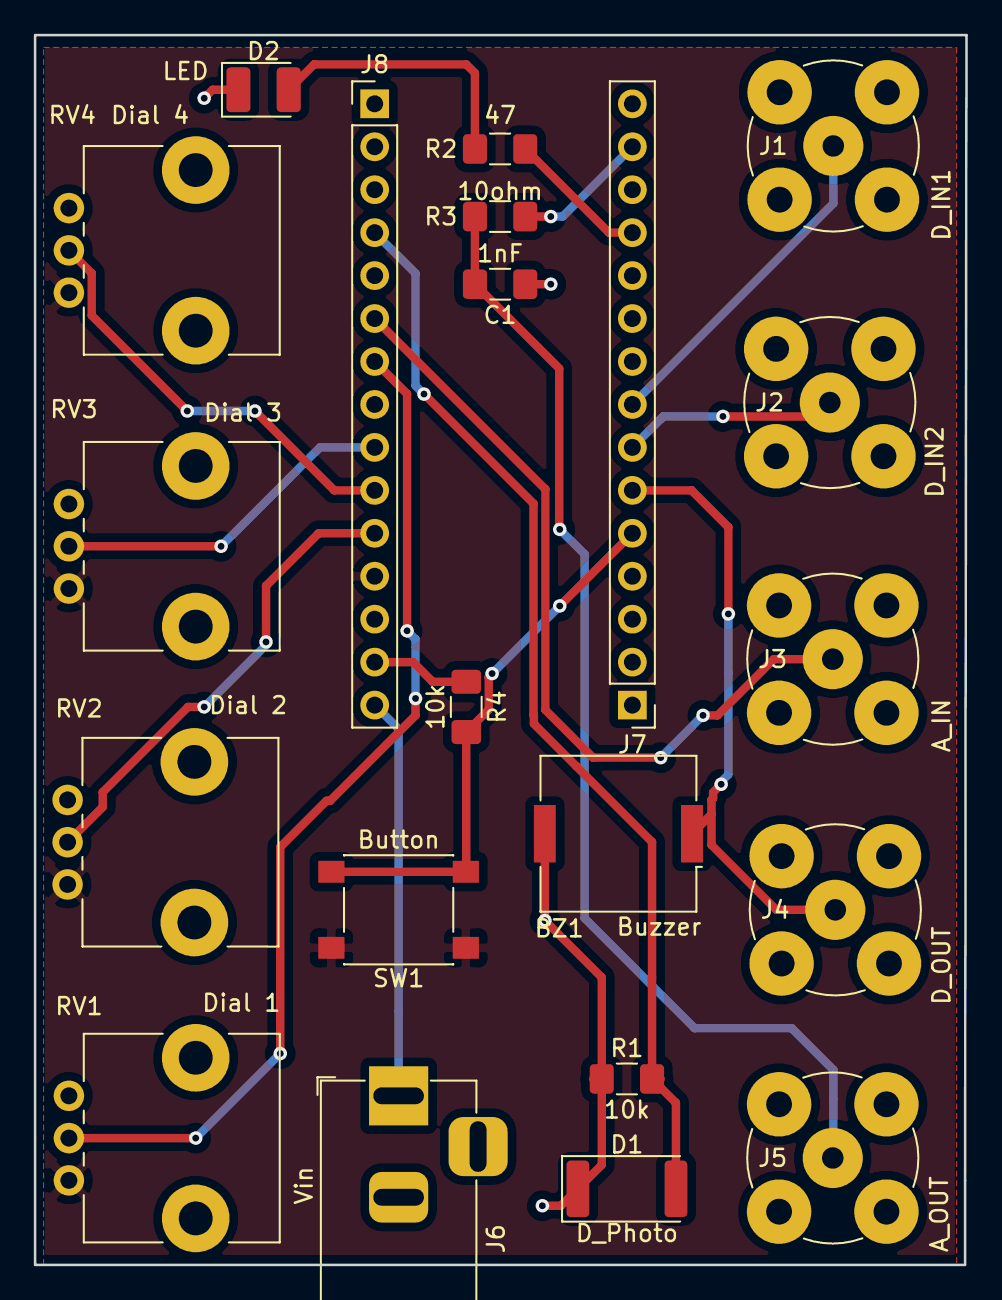
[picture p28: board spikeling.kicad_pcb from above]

Board: 2 copper layers, 55.1 x 72.7 mm, 21 parts (0 on the bottom side), 17 nets.

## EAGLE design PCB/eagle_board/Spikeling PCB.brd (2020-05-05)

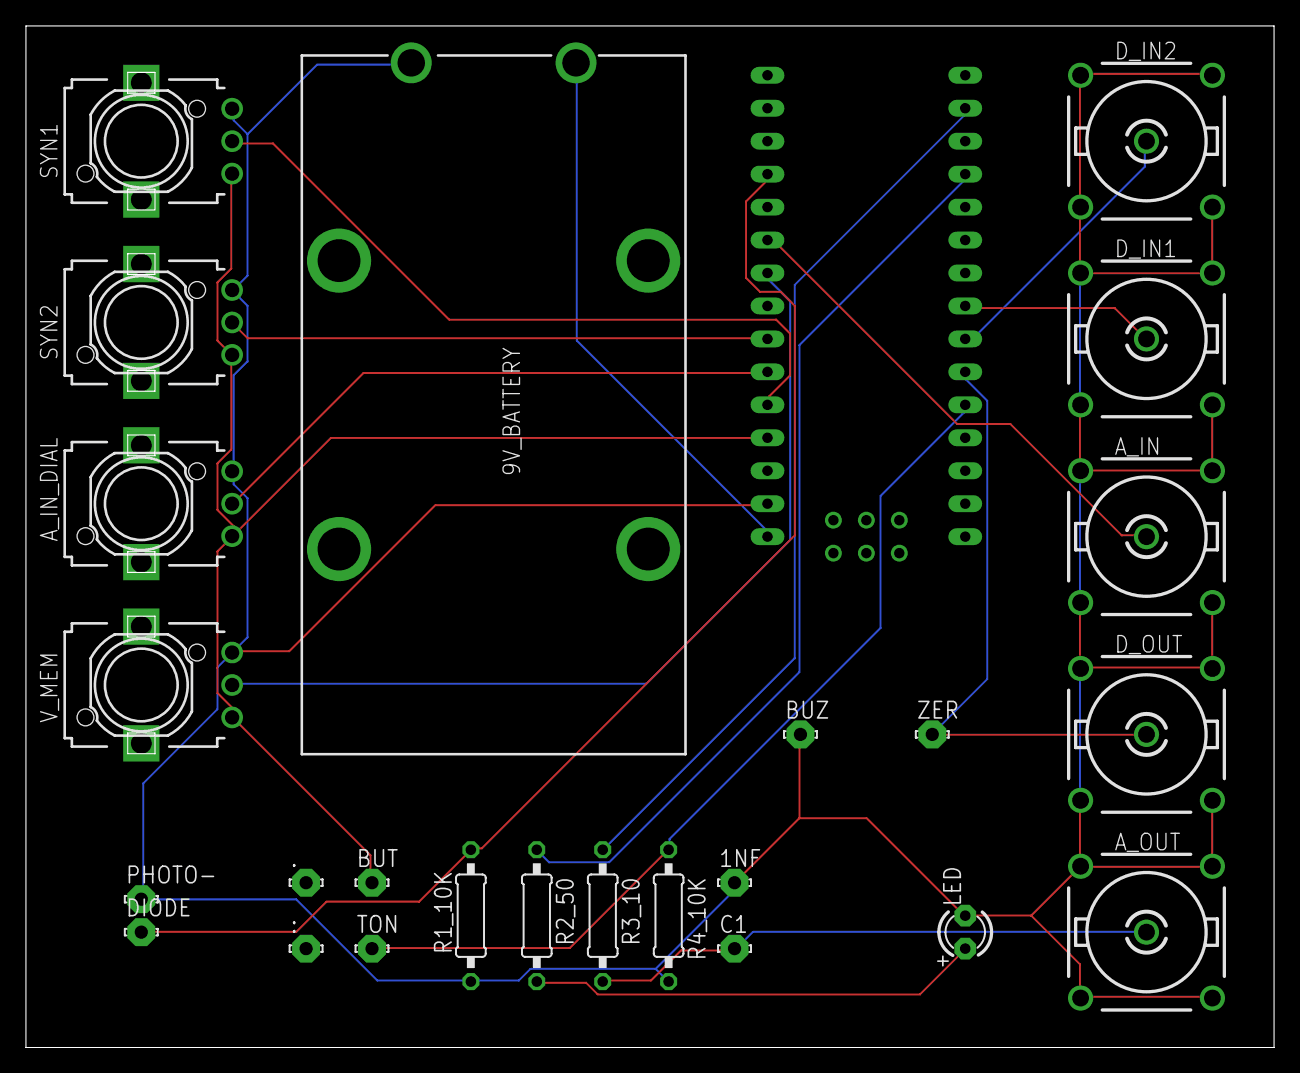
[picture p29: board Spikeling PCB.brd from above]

Board: 2 copper layers, 96.2 x 78.7 mm, 26 parts (0 on the bottom side), 17 nets.

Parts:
1NF, .: LSP10
9V_BATTERY: 1294
:: LSP10
A_IN: BNC; R141426
A_IN_DIAL: EVUFXL
A_OUT: BNC; R141426
BUT: LSP10
BUZ: LSP10
C1: LSP10
DIODE: LSP10
D_IN1, D_IN2: BNC; R141426
D_OUT: BNC; R141426
LED: LED3MM
PHOTO-: LSP10
R1_10K: 220; 0207/10
R2_50: 50; 0207/10
R3_10: 10; 0207/10
R4_10K: 10k; 0207/10
SYN1, SYN2: EVUFXL
TON: LSP10
U$1: NANO
V_MEM: EVUFXL
ZER: LSP10

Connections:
GND: 1NF.MP, 9V_BATTERY.2, A_IN.2, A_IN.3, A_IN.4, A_IN.5, A_IN_DIAL.3, A_OUT.2, A_OUT.3, A_OUT.4, A_OUT.5, BUZ.MP, D_IN1.2, D_IN1.3, D_IN1.4, D_IN1.5, D_IN2.2, D_IN2.3, D_IN2.4, D_IN2.5, D_OUT.2, D_OUT.3, D_OUT.4, D_OUT.5, LED.K, PHOTO-.MP, R1_10K.1, R4_10K.2, SYN1.3, SYN2.3, U$1.GND, V_MEM.3
unnamed: R3_10.1, U$1.D11
unnamed: A_OUT.1, C1.MP, R3_10.2
unnamed: DIODE.MP, R1_10K.2, U$1.A0
unnamed: R2_50.1, U$1.D9
unnamed: LED.A, R2_50.2
unnamed: 9V_BATTERY.1, U$1.RAW
unnamed: U$1.A3, V_MEM.2
unnamed: D_IN2.1, U$1.D4
unnamed: R4_10K.1, TON.MP, U$1.D2
unnamed: D_OUT.1, U$1.D3, ZER.MP
unnamed: D_IN1.1, U$1.D5
unnamed: SYN1.2, U$1.A7
unnamed: A_IN_DIAL.2, U$1.A6
unnamed: A_IN.1, U$1.A2
unnamed: SYN2.2, U$1.A5
unnamed: A_IN_DIAL.1, BUT.MP, SYN1.1, SYN2.1, U$1.5V, V_MEM.1

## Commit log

2020-05-05 organize repo
    [B.Cu.gbr, B.Mask.gbr, B.Paste.gbr, B.SilkS.gbr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]
2020-05-05 organize repo, port kicad boards
    [spikeling.kicad_pcb, spikeling.sch]
2020-05-17 create SMD board
    [BOM_circuit_hub.csv, spikeling-B_Adhes.gbr, spikeling-B_CrtYd.gbr, spikeling-B_Cu.gbr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]
2020-06-08 update smd version of board
    [spikeling-B_Adhes.gbr, spikeling-B_CrtYd.gbr, spikeling-B_Cu.gbr, spikeling-B_Fab.gbr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]
2020-07-09 more work on smd board
    [spikeling-B_Adhes.gbr, spikeling-B_CrtYd.gbr, spikeling-B_Cu.gbr, spikeling-B_Fab.gbr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]
2020-07-16 update SMD board
    [1-click_BOM.tsv, spikeling-B_Adhes.gbr, spikeling-B_CrtYd.gbr, spikeling-B_Cu.gbr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]
2021-04-26 modified kicad pcb
    [BOM_001_spikeling1.xls, BOM_circuit_hub.csv, BOM_seeed.csv, spikeling-B_Adhes.gbr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]

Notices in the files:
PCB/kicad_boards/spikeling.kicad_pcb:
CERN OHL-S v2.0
